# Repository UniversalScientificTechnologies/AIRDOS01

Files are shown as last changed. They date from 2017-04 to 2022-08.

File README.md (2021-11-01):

# Airborne dosimeter device - AIRDOS

Cosmic radiation dosimeter unit. It is intended for airborne measurement of cosmic radiation and dosimetry in mixed ionization fields on board of aircraft. 

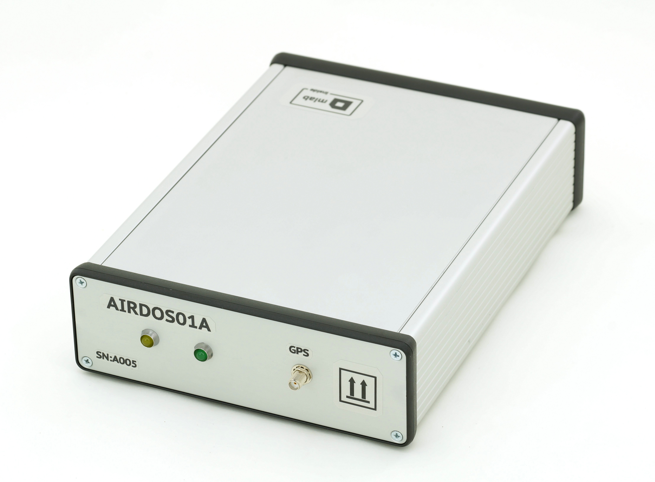
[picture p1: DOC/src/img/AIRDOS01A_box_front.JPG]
AIRDOS01A Front panel with indicating LEDs and GPS antenna connector AIRDOS Front panel


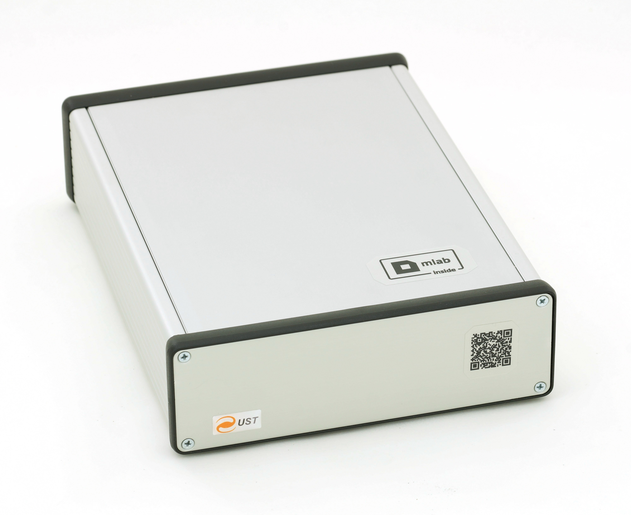
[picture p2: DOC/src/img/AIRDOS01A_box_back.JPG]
AIRDOS01A back panel AIRDOS back panel


Technical parameters are following: 

* Silicon PIN diode detector with 60mm³ detection volume
* Measurement endurance 32 days
* Number of erengy channels    252
* Energy measurement resolution    <30 keV/channel
* GPS logging interval    5 minutes
* Time to GPS fix	26 s
* Airborne GPS parameters (Navigation altitude verified up to 36km amsl)
* Integration time    8 s
* Weight 1.225 kg (Without batteries and GPS antenna)

Device block diagram
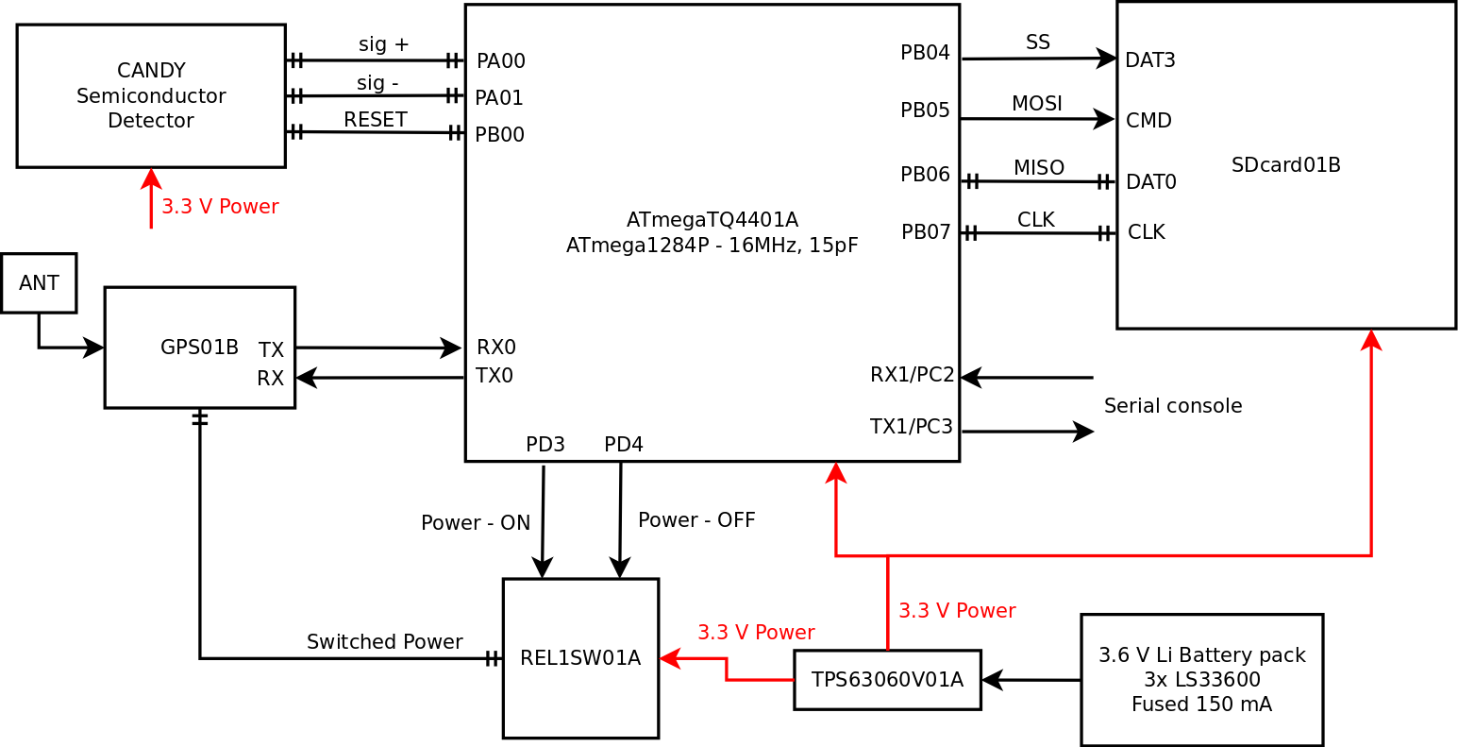
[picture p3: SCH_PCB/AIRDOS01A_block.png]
AIRDOS01A back panel


CANDY detector schematics
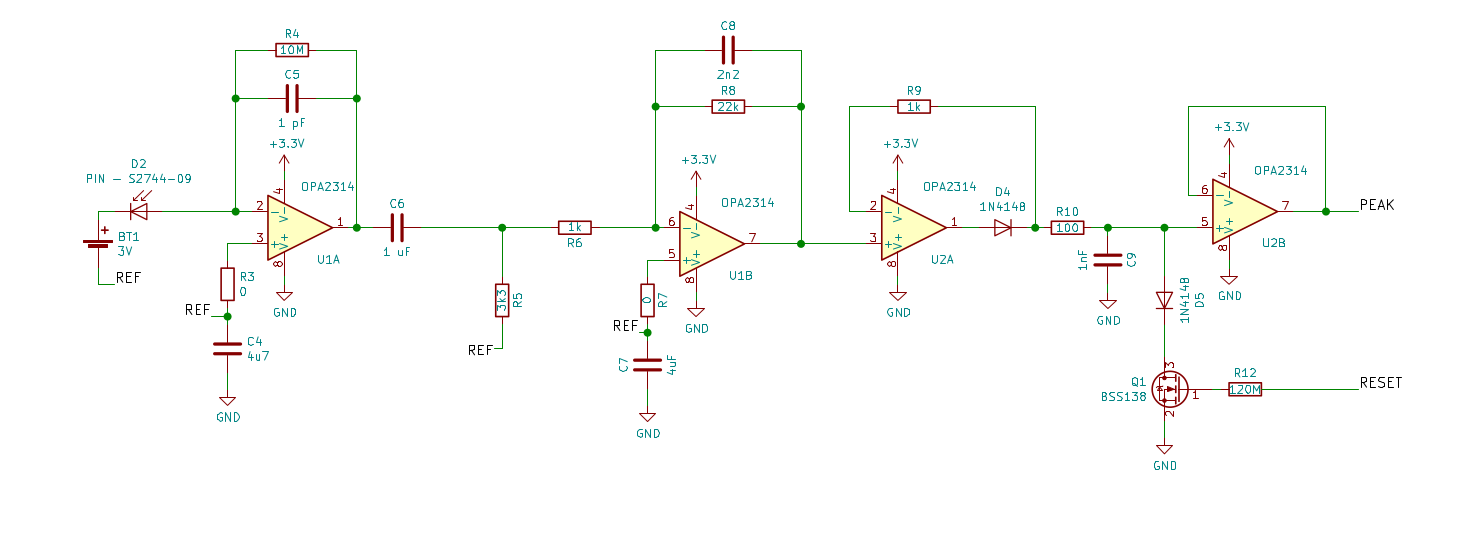
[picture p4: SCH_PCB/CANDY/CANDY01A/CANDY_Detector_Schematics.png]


The device is replaced with updated version [AIRDOS02](https://github.com/UniversalScientificTechnologies/AIRDOS02).

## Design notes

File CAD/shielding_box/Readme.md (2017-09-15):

# Manufacturing process

The models could be printed from PLA plastic. The used color filling probably affects intsrument sensitivity. Use of natural PLA material is recommended. 

  * Parts must be coated by copper conductive layer
  * Printed parts need cleanup after printing. Cleanup is mandatory operation before coating.

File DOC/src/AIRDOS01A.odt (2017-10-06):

AIRDOS01E

Seznam materiálu:

GPS01B

-JUMP -EXT

-USB-OFF

-ACTIVE

REL1SW01A

-JUMP -VCC-1

-1-2

-VCC-10

TPS63060V01A

-JUMP -EN-VIN

-MODE

-3,3V

ATMEGATQ4401A

-krystal 16MHz

SDcard01B

-bez LED

M3x14 8ks – na OZDUAL03B -dotahují se pak všechny matky, nesmí se nic klepat

Přední panel boxu:

Pořadí prvků na panelu z leva do prava: LED ŽLUTÁ, LED ZELENÁ, SMA

LED ZELENÁ – 5mm, odpor na anodu 1kΩ, vodiče 10 cm

LED ZELENÁ/A – GPS01B/TIMEPULSE – zelená

LED ZELENÁ/K – GPS01B/GND – modrá

LED ŽLUTÁ – 5mm, odpor na anodu 1kΩ, vodiče 13 cm

LED ŽLUTÁ/A – ATMEGATQ4401A/VCC – žlutá

LED ŽLUTÁ/K – ATMEGATQ4401A/PC7 – modrá

OZDUAL03B č.1

-JUMP -GNDA-GND

Baterka 3V

-přidělané káblíky 4,5 cm, žlutá +, modrá -. Konektroy na hřebínek na konci.

Baterkové pouzdro na 3 baterie

-kabel s pojistkou + 5 cm kabelu – červená

-20cm - modrá

OZDUAL03B č.2

-JUMP - GNDA-GND

- 5 – 4

- OUTA – INA-

Detektor

ATMEGATQ4401A – OZDUAL03B č.1

PA1 – INB+ - bílá 15 cm

ATMEGATQ4401A – OZDUAL03B č.2

PB0 – 1 - fialová 15 cm

GND – GNDA - modrá 15 cm

VCC – VIN+ - červená 15cm

PA0 – OUTB – žlutá 15cm

Baterie 3V – OZDUAL03B č.1

- - INA+ - žlutá

+ - VREF – modrá

OZDUAL03B č.2 – OZDUAL03B č.1

POWER – POWER – vodič modrý a červený 10 cm

VREFA – OUTB – žlutá 10 cm

OZDUAL03B č.2

VREFB – 2 – šedá 10 cm

INB+ - OUTA – žlutá 10 cm

OZDUAL03B č.1

VREFA – 2 – 4 – INB+ - fialová 10 cm

VREFB – OUTA – žlutá 10 cm

ATMEGATQ4401A

AREF – PA1 – bílá 10 cm

PC2 – VCC – oranžová 10 cm

10K (proti přívodu z GPS) – PD0 – oranžová 10 cm

ATMEGATQ4401A – Sdcard01B

PB7 – J4 – fialová 15 cm

PB6 – J5 – bílá 15 cm

PB5 – J3 – oranžová 15 cm

PB4 – J8 – šedá 15 cm

POWER – POWER 3,3V – modrá/červená 20 cm

ATMEGATQ4401A – TPS63060V01A

POWER – POWER OUT – červená/modrá 10 cm

RELL1SW01A – ATMEGATQ4401A

IN2 – PD3 – bílá 10 cm

IN1 – PD4 – šedá 10 cm

RELL1SW01A

5 – OUT1 – zelená 10 cm

6 – OUT2 – fialová 10 cm

RELL1SW01A – TPS63060V01A

POWER – POWER IN – červená/modrá 10 cm

RELL1SW01A – GPS01B

POWER (-) – POWER – modrá 10 cm

3 – POWER – červená 10 cm

GPS01B – ATMEGATQ4401A

TXD – 10k – oranžová 10 cm

RXD – PD1 – žlutá 10 cm

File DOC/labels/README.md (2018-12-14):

### Samolepky na přístroj AIRDOS

Samolepky jsou vytištěné na laminovaných páskách  TZE-111, TZE-121 a TZE-151. 

Po vytištení je potřeba samolepkám diagonálně zastřihnout rohy, aby bylo snížena možnost jejich odloupnutí.  Na přístroj se samolepky lepí podle následujících obrázků.

**Povrch přístroje je potřeba před lepením odmastit gázovým čvercem namočeným v alkoholu!**

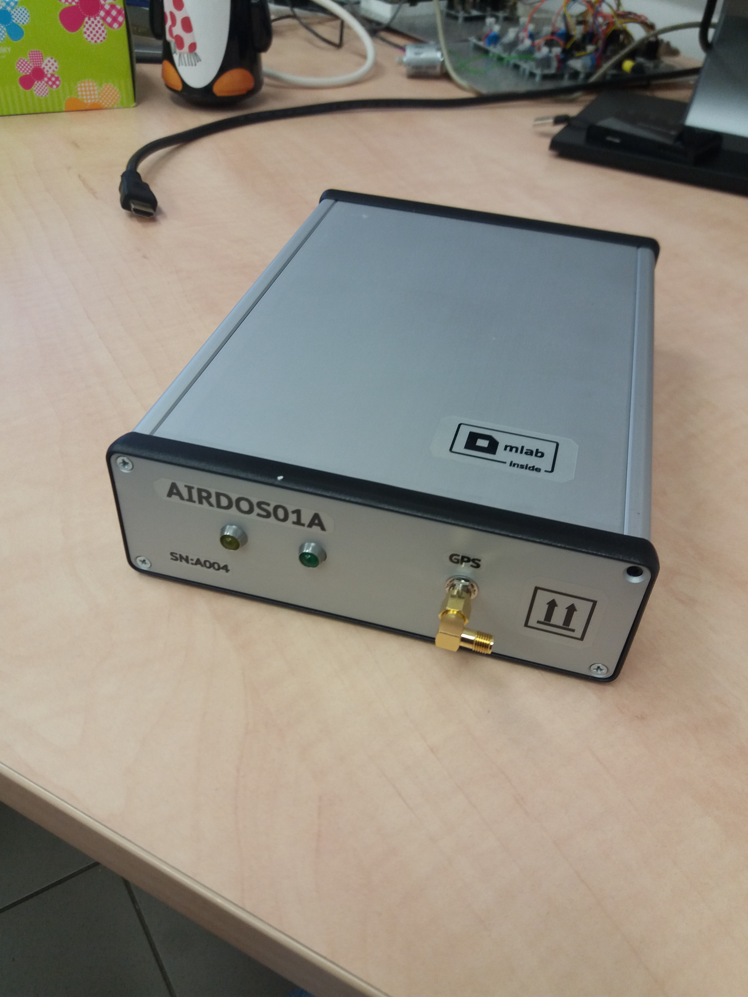
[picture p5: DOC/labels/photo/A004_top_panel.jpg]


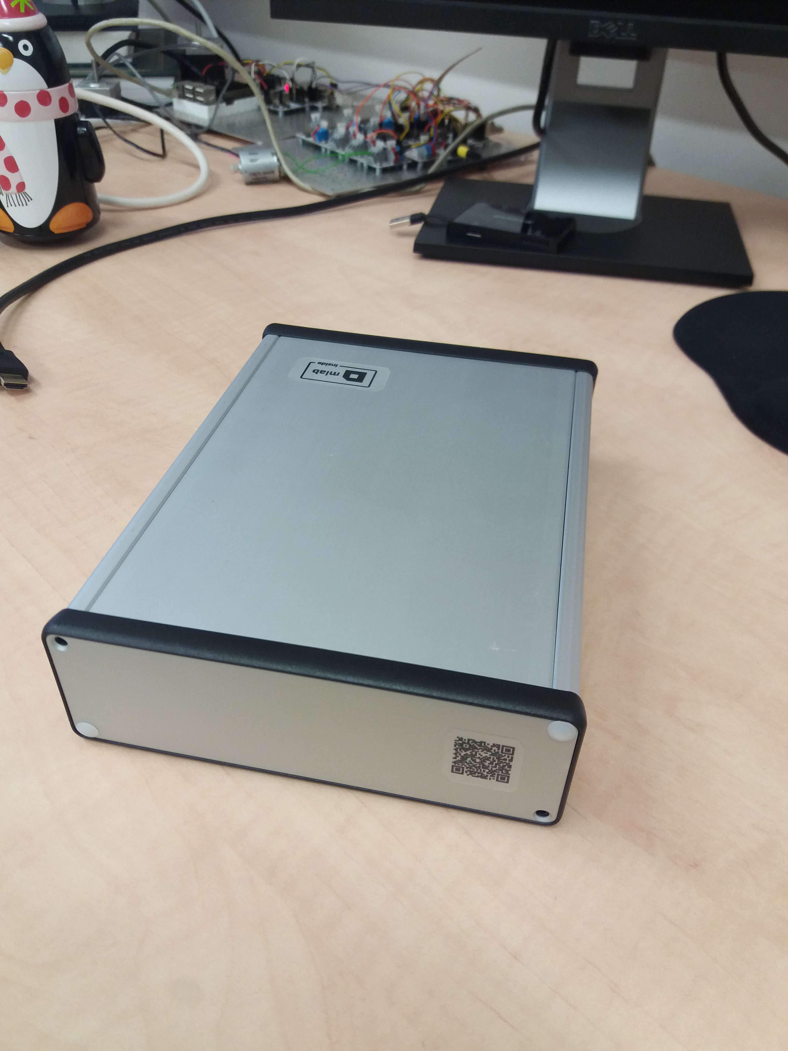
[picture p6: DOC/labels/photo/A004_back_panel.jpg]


Kromě těchto vnitřních samolepek existují ještě vnitřní samolepky se seriovými čísly, které jsou nalepeny na vnitřní stranu vyjmutelných plechových dílů. 

### Generování QRkódů

QR kód se generuje spuštěním příkazu

    ./generate_QR.sh

Ještě před tím je ale potřeba ve skriptu nastavit obsah, který má QRkód obsahovat. 

Tím vznikne soubor AIRDOS01-QRcode.svg, který obsahuje aktualizovaný QRkód. 
Tento soubor je prolinkován se souborem QRcode_24x24.svg ve kterém by se měl automaticky aktualizovat při otevření souboru. 

Soubor QRcode_24x24.pdf je nutné ručně exportovat.

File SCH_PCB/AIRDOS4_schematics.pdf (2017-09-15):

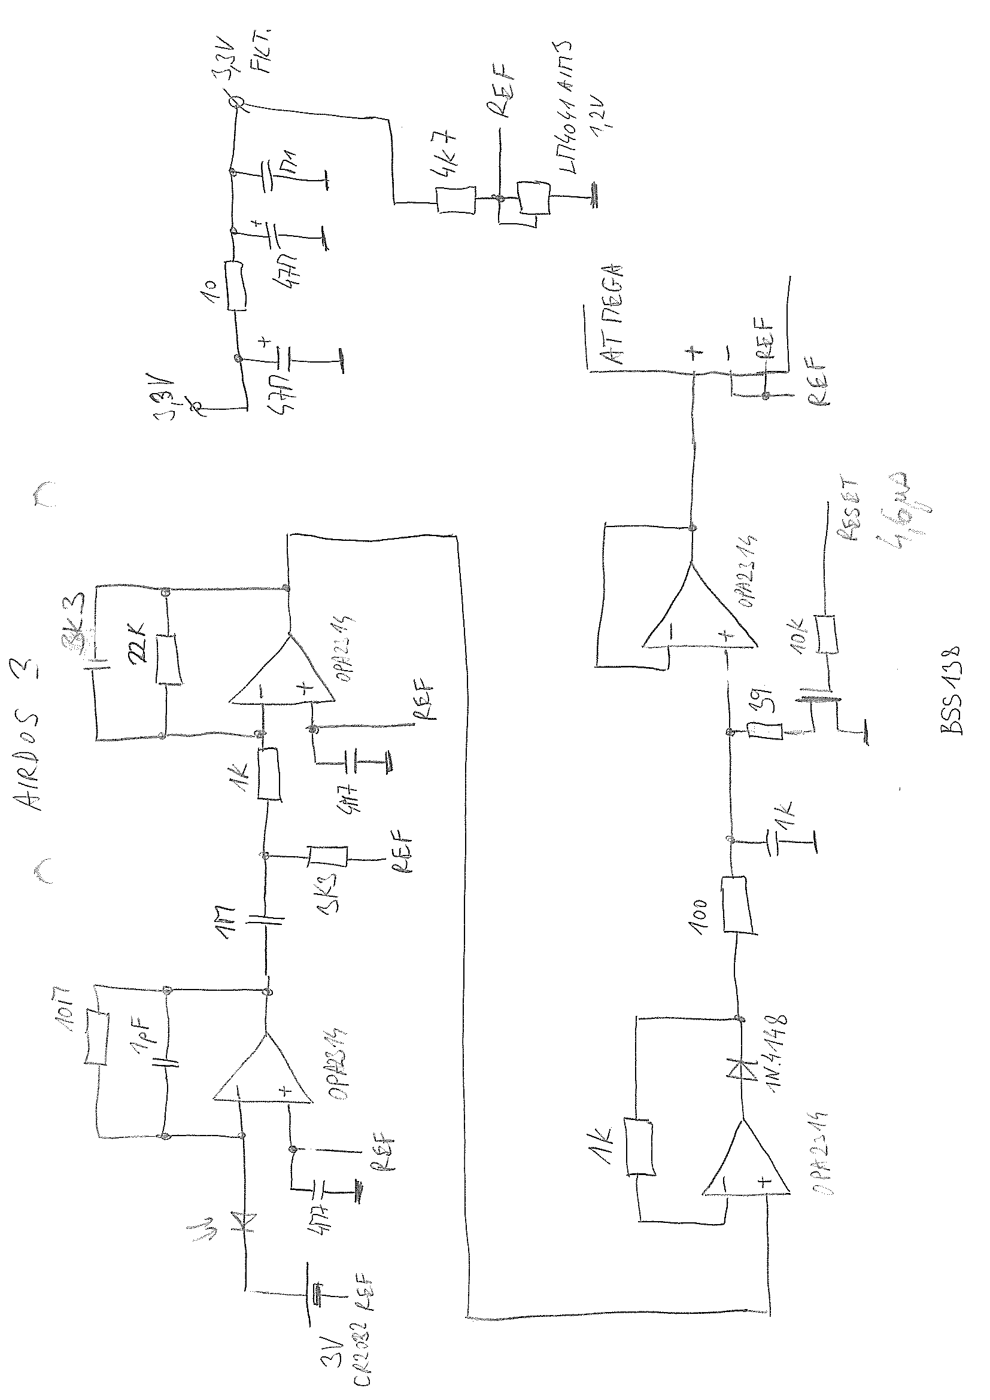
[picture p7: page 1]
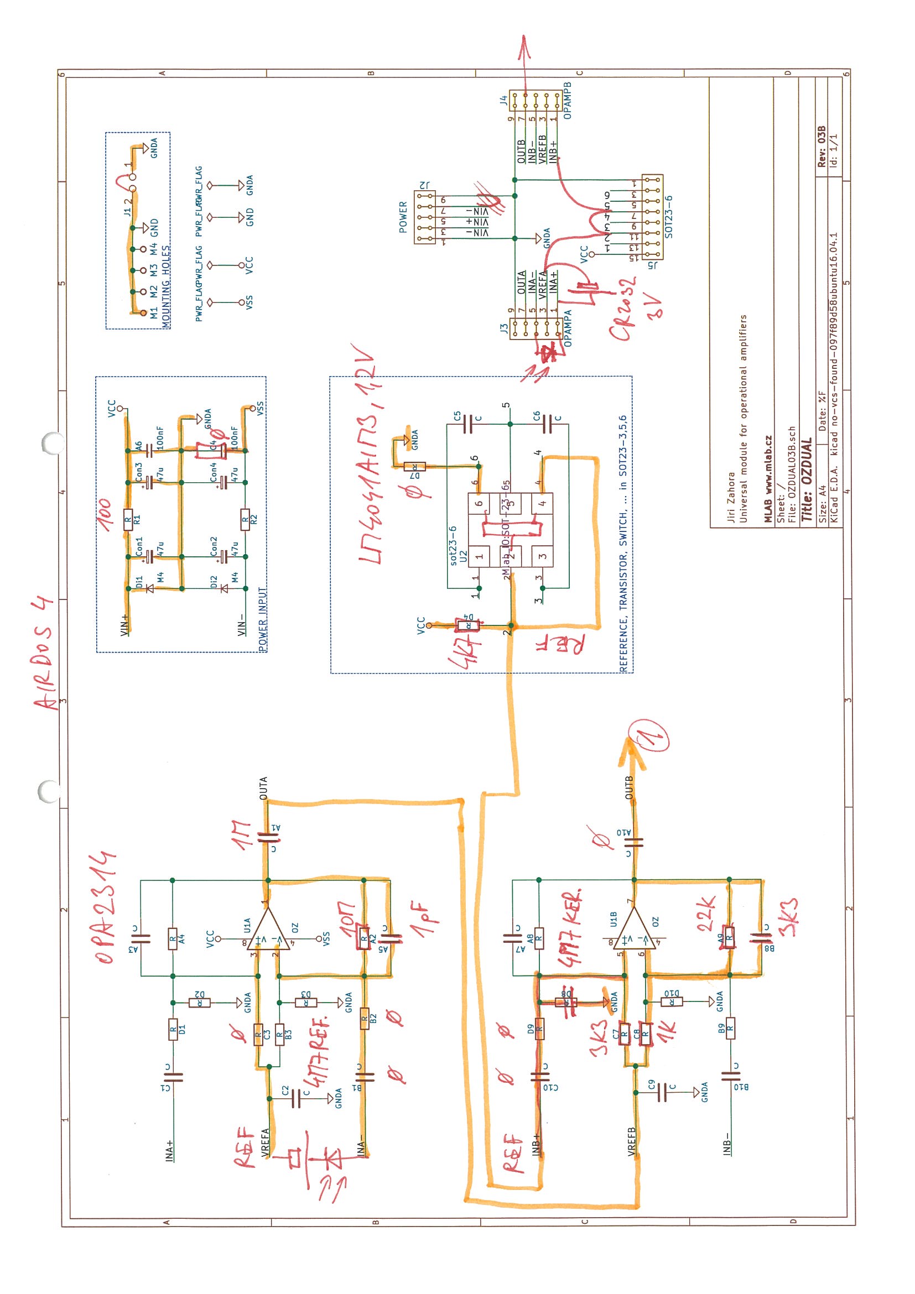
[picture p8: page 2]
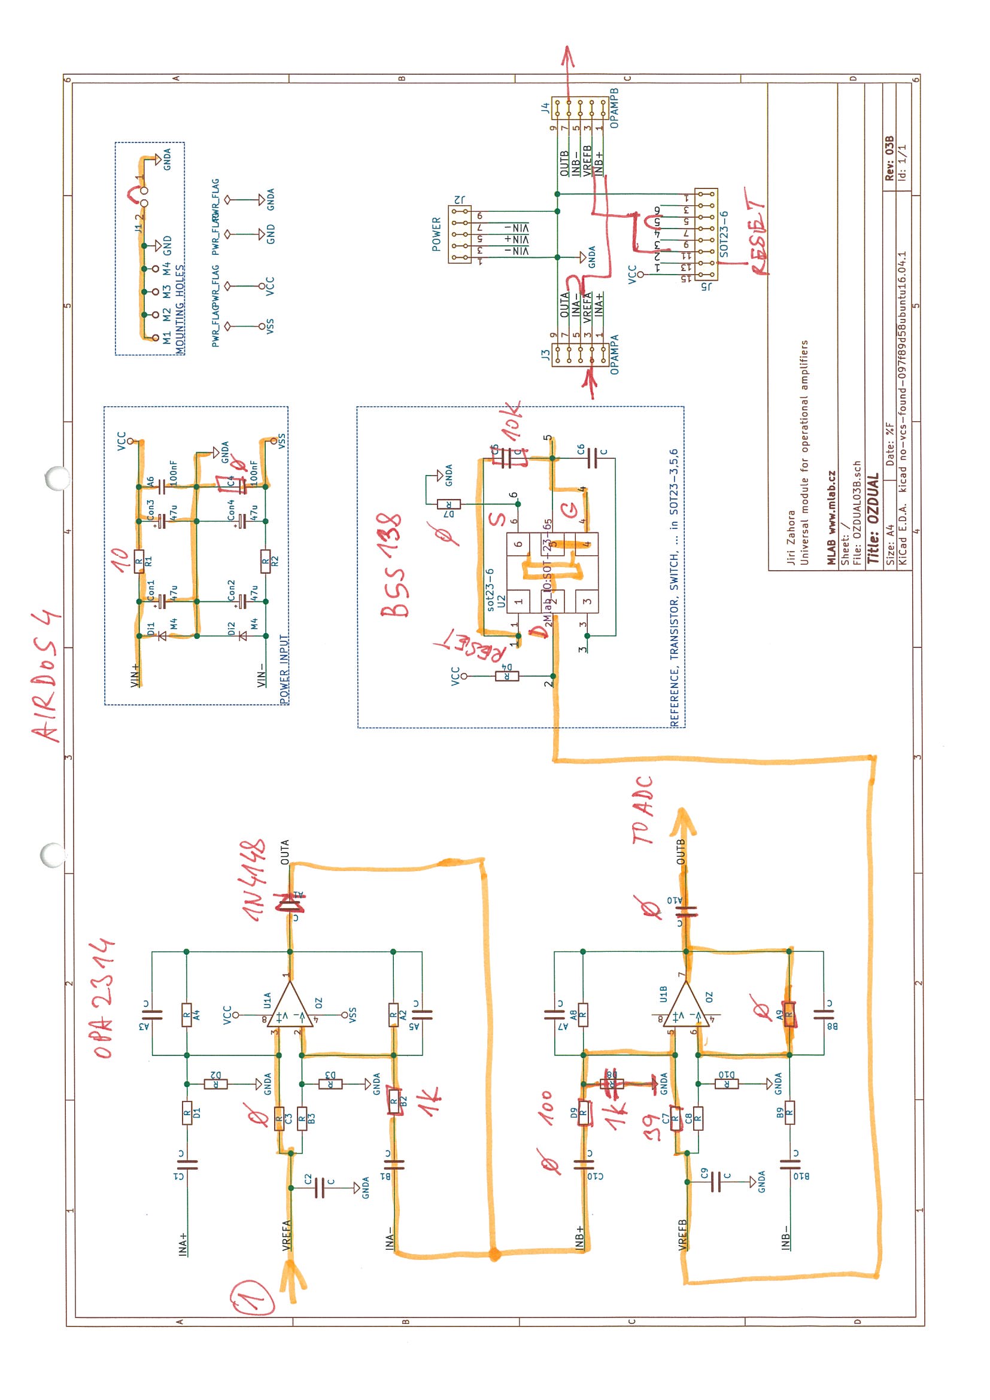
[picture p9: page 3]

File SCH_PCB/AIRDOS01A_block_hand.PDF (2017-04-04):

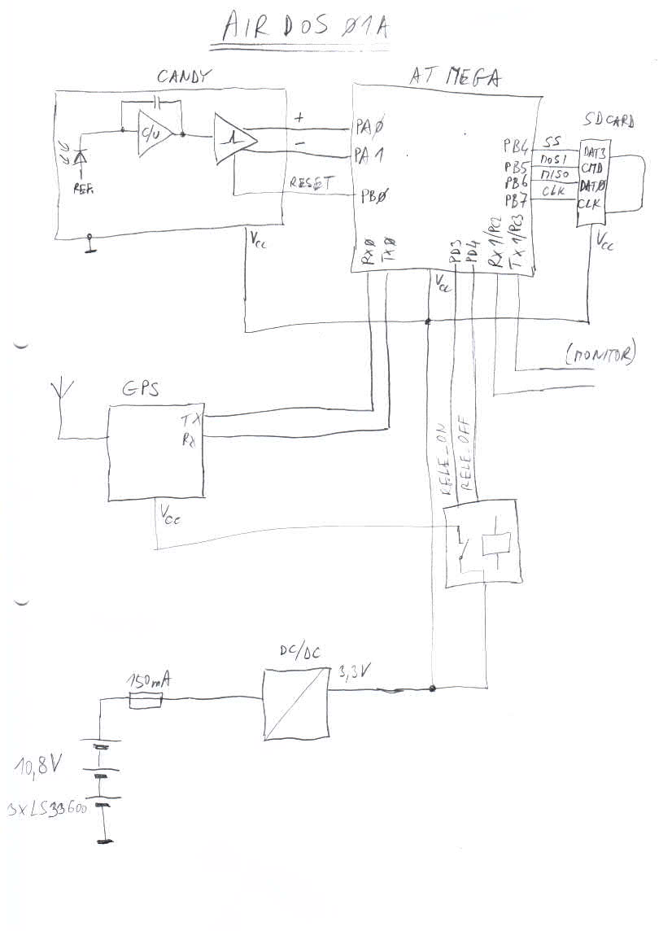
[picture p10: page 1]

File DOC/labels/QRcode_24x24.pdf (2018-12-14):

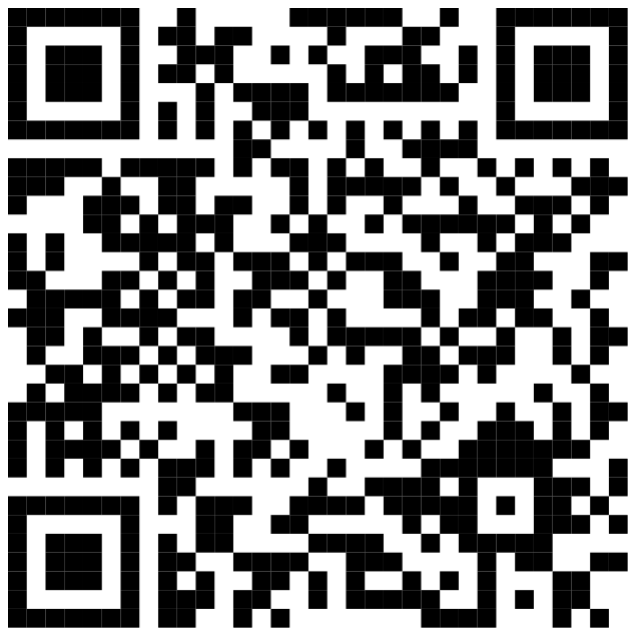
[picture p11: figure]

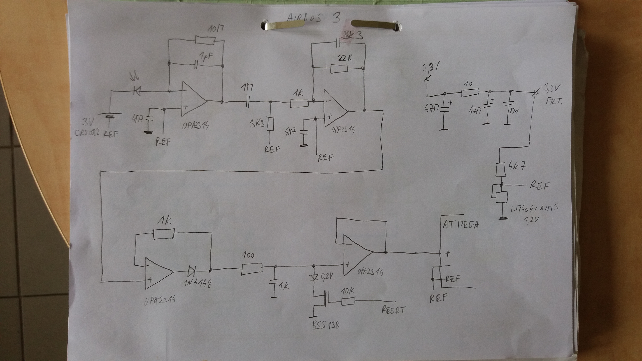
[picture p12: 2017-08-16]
SCH_PCB/AIRDOS3_Schematics.jpg

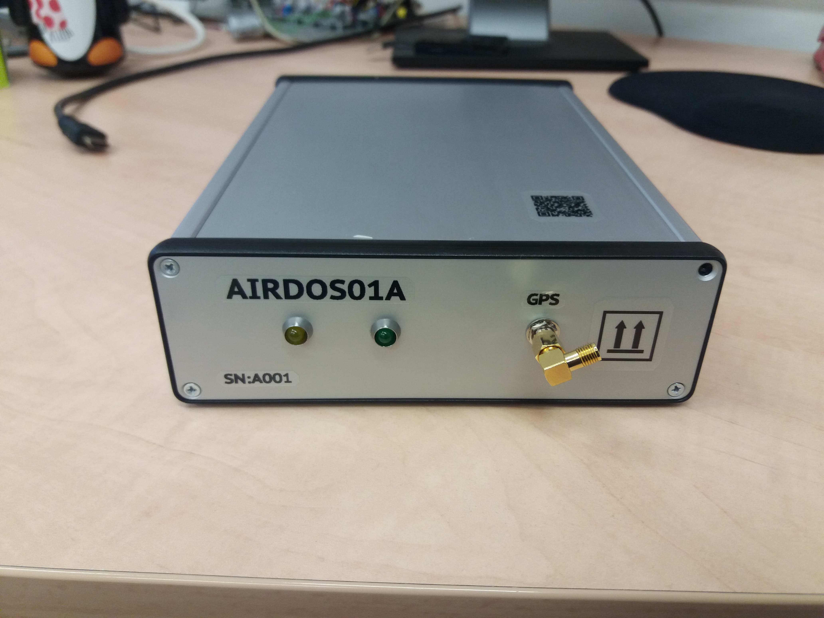
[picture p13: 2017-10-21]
DOC/labels/photo/A001_front_panel.jpg

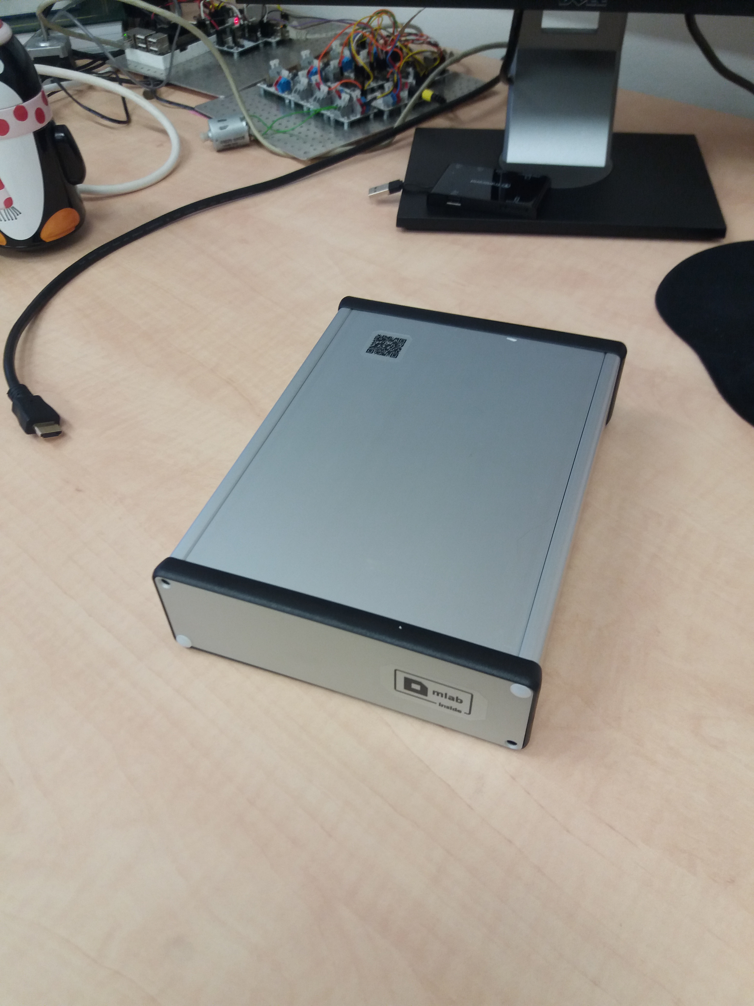
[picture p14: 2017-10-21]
DOC/labels/photo/A001_back_panel.jpg

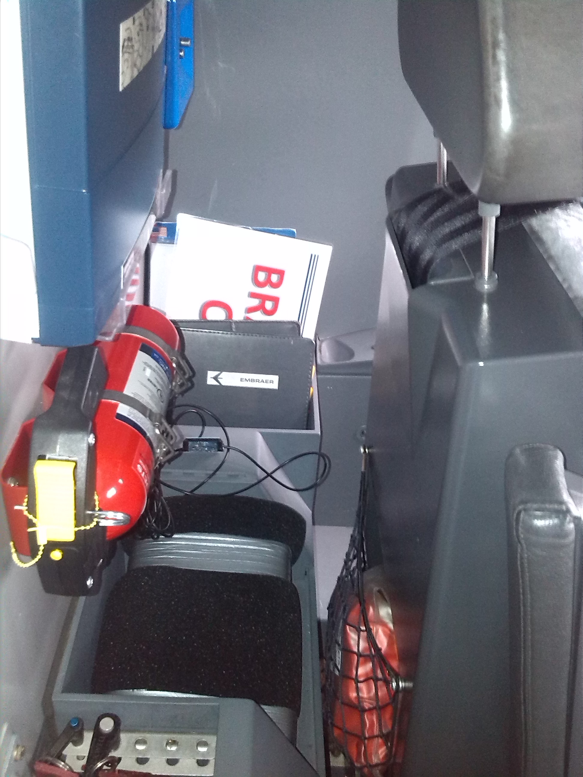
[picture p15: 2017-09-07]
DOC/src/img/AIRDOS01A_in_use.jpg

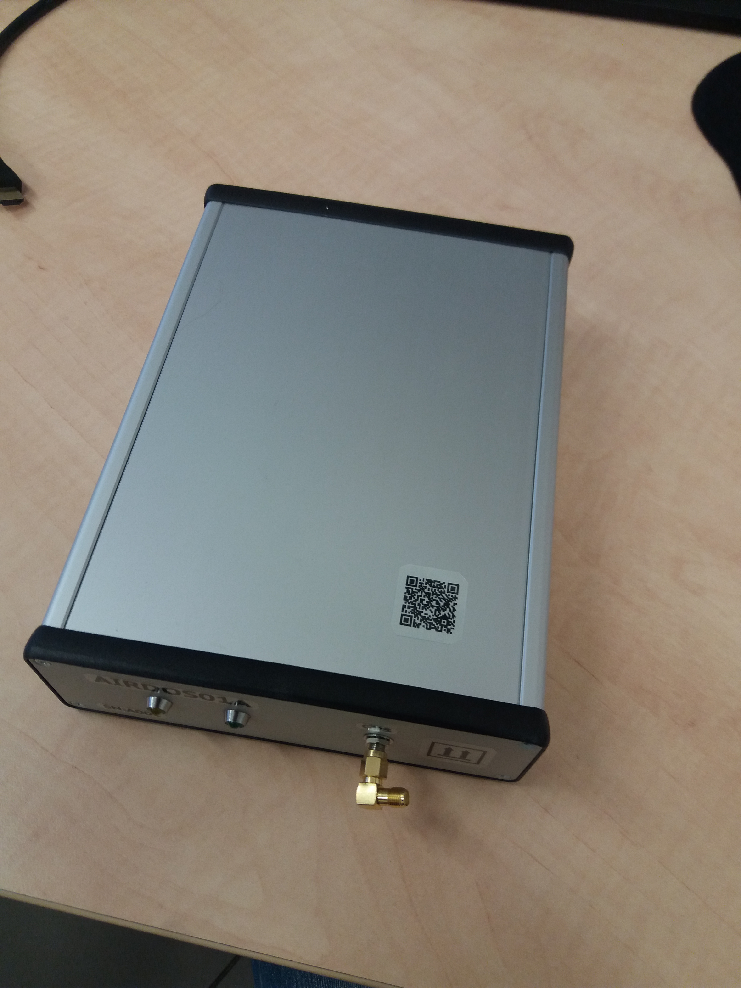
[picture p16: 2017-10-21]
DOC/labels/photo/A001_top_cover.jpg

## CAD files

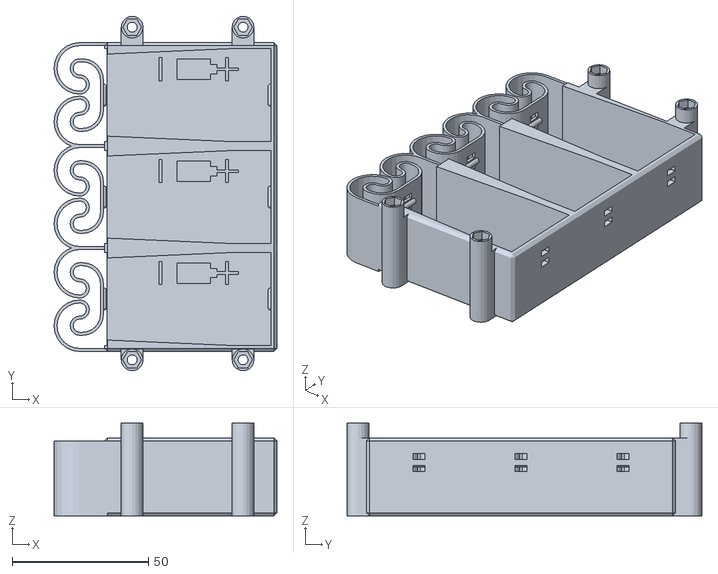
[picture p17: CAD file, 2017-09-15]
CAD/Battery_holder/AMF/P_AIRDOS_batter_body.stl
81.7 x 129.9 x 34.0

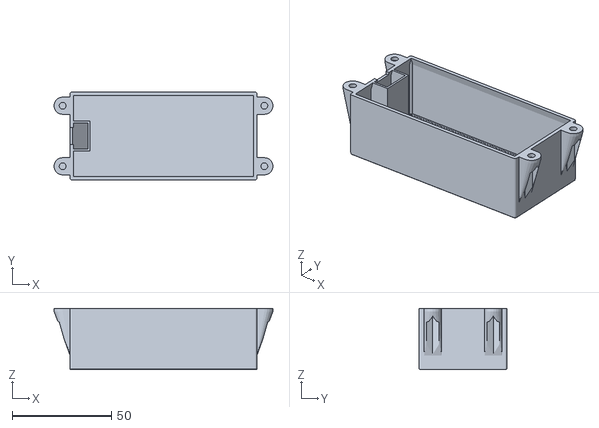
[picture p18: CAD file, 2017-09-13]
CAD/shielding_box/Box.stl
110.3 x 44.2 x 30.9

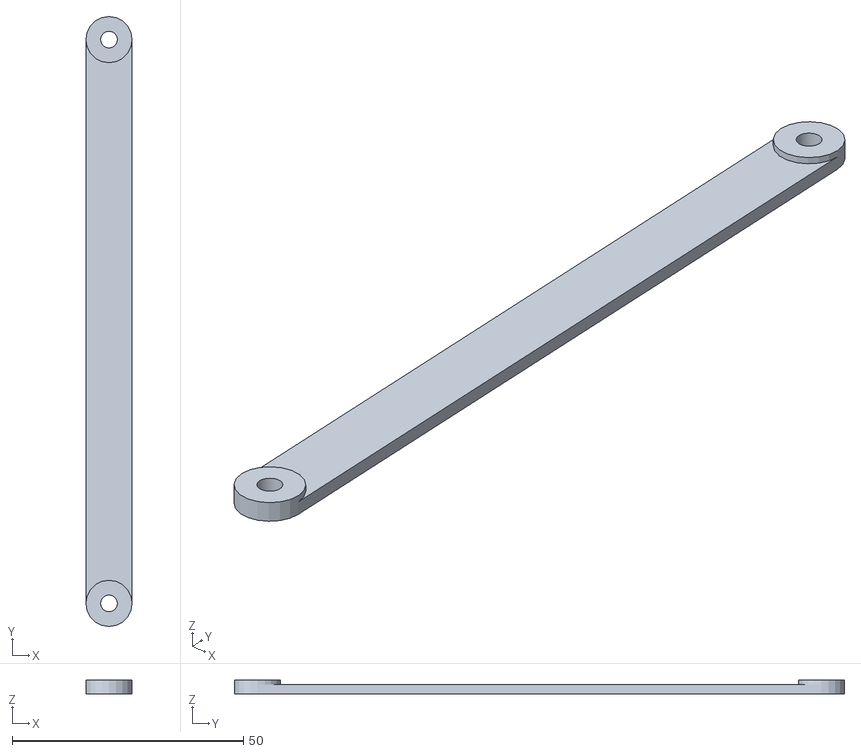
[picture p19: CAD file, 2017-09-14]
CAD/Battery_holder/AMF/P_AIRDOS_batter_belt.stl
10.0 x 131.9 x 3.00

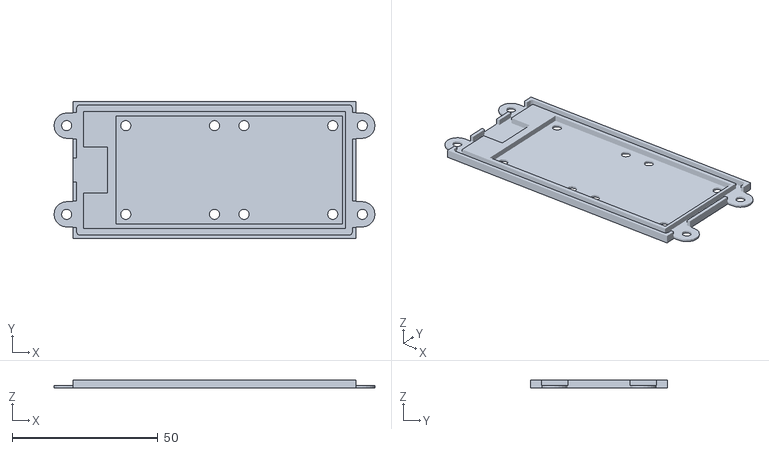
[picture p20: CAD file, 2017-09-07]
CAD/shielding_box/BoxBase.stl
110.3 x 47.2 x 2.80

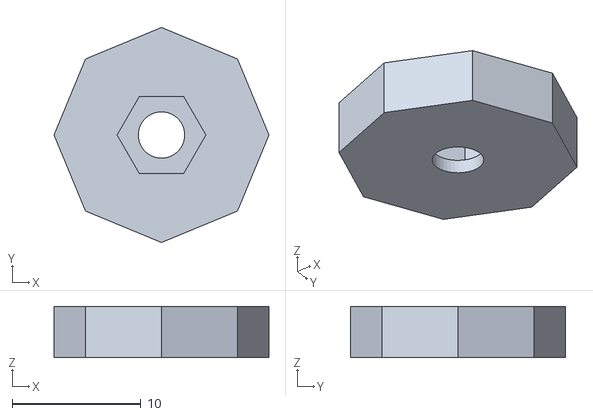
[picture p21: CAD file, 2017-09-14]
CAD/Battery_holder/AMF/P_AIRDOS_batter_nut.stl
16.7 x 16.7 x 4.00

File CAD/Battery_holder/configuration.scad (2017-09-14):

//Parametry sroubu
prumer_sroubu=3.4;
prumer_hlavy_sroubu=6;
vyska_hlavy_sroubu=4;
vyska_matky=3;
sirka_matky=6.7;

baterka_prumer=33;
baterka_delka=60;


vyska_sloupku=baterka_prumer+1;
sila_materialu=1.3;

pocet_poli_mezi_srouby=12;

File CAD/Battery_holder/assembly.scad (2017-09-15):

use <src/flexbatter.scad>
use <src/AIRDOS_batter.scad>

include <configuration.scad>


AIRDOS_prezentace();

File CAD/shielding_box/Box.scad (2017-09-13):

h = 30;      // Výška horní části
s = 4;      // Výška spodní části
a = 4;       // Šířka krabičky (počet obsazených dírek)
b = 9;      // Délka krabičky (počet obsazených dírek)
d = 1.8;     // Průměr trnů a šířka hlavních příček (>1)
c = 0.8;   // Tloušťka stěn

drat = 1.5;  // Průměr/výška otvoru na dráty

okraj = 2;  // šířka horního okraje

clear = 0.4;      // K otvoru na matičku
nut_size = 6.6;     // K otvoru na matičku

MLAB_grid = 10.16;
pedestal_height = 2; 

ot = 6*MLAB_grid/11;         //Vzdálenost okraje od děr v plošňáku pro stranu s tunelem
o = MLAB_grid/2+d/2;   //Vzdálenost zbylých okrajů od děr v plošňáku



$fn=20;

roh =0.5; // Zaoblení hran

// Kvádr a válec se zaoblenými hranami
module roundcube(size,center=true,corner) {
  minkowski() {
    cube(size,center);
    sphere(corner);
  }
}

module roundcylinder(size, r, center=true, corner) {
  minkowski() {
    cylinder(size, r, r, center);
    sphere(corner);
  }
}







module konstrukce1()
{
  difference() {
  union() {
      // Hlavní příčky
     translate([0,(MLAB_grid*(a-1))/2+o,0]) 
      roundcube([d-2*roh, MLAB_grid*(a-1)+2*o, d-2*roh],center = true, corner= roh);
     
     translate([(MLAB_grid*(b-1))/2+ot,0,0])       
      roundcube([MLAB_grid*(b-1)+2*ot, d-2*roh, d-2*roh],corner= roh); 
      
     translate([0, 0, h/2])
      cylinder(h, d/2, d/2, center = true);
      
 /*     //Vedlejší příčky - ve směru x
      for(i = [1:a]) {
     translate([(MLAB_grid*(b-1))/2+ot ,o + MLAB_grid*(i-1),-d/4+roh/2])
      roundcube([MLAB_grid*(b-1)+2*ot,d-2*roh,(d-2*roh)/2],corner = roh);
      }
      //Vedlejší příčky - ve směru y
      for(i = [1:b]) {
     translate([ot + MLAB_grid*(i-1), (MLAB_grid*(a-1))/2+o, -d/4+roh/2])
      roundcube([d-2*roh, MLAB_grid*(a-1)+2*o, (d-2*roh)/2],corner=roh);
      }
      //Vedlejší příčky - ve směru z
      for(i = [1:a]) {
     translate([0, o + MLAB_grid*(i - 1), h/2])
      difference() {
          cylinder(h, d/2, d/2, center = true);
          translate([d/2,0,h/2])
          cube([d,d,h/2+5], center = true);
      }
      }
      for(i = [1:b]) {
     translate([ot+MLAB_grid*(i-1), 0, h/2])
      cylinder(h, d/2, d/2, center = true);
      }
      
  */    
 // ZAOBLENI ROHU    
  hull() {
difference() {
            union() {
    translate([0,(MLAB_grid*(a+1))/2,0]) 
      roundcube([d-2*roh,MLAB_grid*(a+1),d-2*roh],center = true, corner= roh);
     
     translate([(MLAB_grid*(b+1))/2,0,0])       
      roundcube([MLAB_grid*(b+1),d-2*roh,d-2*roh],corner= roh); 
      
     translate([0, 0, h/2-d/2+2*roh])
      roundcylinder(h, (d/2-roh), corner = roh);
            }
      translate([0,(MLAB_grid*(a+1))/2 + d,0]) 
        cube([20*d,MLAB_grid*(a+1)+d,20*d], center = true);
     
      translate([(MLAB_grid*(b+1))/2 + d,0,0]) 
        cube([MLAB_grid*(b+1)+d,20*d,20*d], center = true);
            
      translate([0, 0, -d/2 + d])
        cylinder(h + d, 20*d);
        }
    }
   

 //Pacička

translate([ot-MLAB_grid, o,h-1.5]) {
    difference() {  
        hull() {
        translate([0,-3/7*MLAB_grid,0])
            cube([MLAB_grid-ot-0.2,2*3/7*MLAB_grid,1.5]);
            cylinder(1.5, 3/7*MLAB_grid, 3/7*MLAB_grid);
        translate([MLAB_grid-ot-c, -3/7*MLAB_grid, -3*h/4])
            cube([c-0.2, 2*3/7*MLAB_grid, 1.5]);
        }
    translate([0,0,1.5/2+0.4])   
    cylinder(3, 3.5/2, 3.5/2, center = true);
    translate([0,0,-h/2])
    rotate(0)
    cylinder (h-1.5, r= (nut_size+clear)/2, center = true, $fn=6);
    } 
}

  
}

/* // Oříznutí sloupků
translate([0,0, h - 10]) 
        cube([MLAB_grid*(b)+o,MLAB_grid*(a)+o,20*d]); */
    
/* //Pacička

translate([o-MLAB_grid, o,h -d/2]) {
    difference() {  
        union() {
    translate([0,-3.5,0])
    cube([MLAB_grid-o,2*3.5,d/2]);
    cylinder(d/2, 1/3*MLAB_grid, 1/3*MLAB_grid);
        }
        
    cylinder(h, 3.5/2, 3.5/2, center = true);
    } 
}
 
// Horní příčka k pacičce
translate([-d/2, 0, h - d/2])
    cube([d/2,MLAB_grid*(a-1)+2*o,d/2]);

*/

}







}
konstrukce1();

  



//Zrcadlení

translate([MLAB_grid*(b-1)+2*ot,0,0]) 
mirror(1,0,1) konstrukce1();
translate([0,MLAB_grid*(a-1)+2*o,0])
mirror([0,1,0]) konstrukce1();
translate([MLAB_grid*(b-1)+2*ot,0,0]) 
mirror(1,0,1)
translate([0,MLAB_grid*(a-1)+2*o,0])
mirror([0,1,0]) konstrukce1();



// Obal klece
    difference() {
        union() {
translate([-d/2,0,0]) 
cube([c, MLAB_grid*(a-1)+2*o, h]);

translate([0,-d/2,0]) 
cube([(MLAB_grid*(b-1))+2*ot, c, h]);

translate([0,0,-d/2]) 
cube([(MLAB_grid*(b-1))+2*ot, (MLAB_grid*(a-1))+2*o, c]);
            
translate([(MLAB_grid*(b-1))+2*ot+d/2-c,0,0]) 
cube([c, MLAB_grid*(a-1)+2*o, h]);

translate([0,(MLAB_grid*(a-1))+2*o+d/2-c,0]) 
cube([(MLAB_grid*(b-1))+2*ot, c, h]);
            
// Horní příčky
translate([okraj/2-d/2, (MLAB_grid*(a-1)+2*o)/2, h-1.5*okraj])
   difference() {
    cube([okraj,MLAB_grid*(a-1)+2*o,3*okraj], center = true);  
    translate([okraj/2,0,0])
    rotate([0,15,0])
    cube([okraj,MLAB_grid*(a-1)+2*o,10*okraj], center = true);   
   } 
        
translate([(MLAB_grid*(b-1))+2*ot-okraj/2+d/2, (MLAB_grid*(a-1)+2*o)/2, h - 1.5*okraj])
    difference() {
    cube([okraj,MLAB_grid*(a-1)+2*o, 3*okraj], center = true);
    translate([-okraj/2,0,0])    
    rotate([0,-15,0])
    cube([okraj,MLAB_grid*(a-1)+2*o,10*okraj], center = true);   
   } 
        
translate([(MLAB_grid*(b-1)+2*ot)/2, okraj/2-d/2, h - 1.5*okraj])
    difference() { 
   cube([MLAB_grid*(b-1)+2*ot, okraj, 3*okraj], center = true);
  
   translate([0,okraj/2,0])
    rotate([-15, 0, 0])
   cube([MLAB_grid*(b-1)+2*ot, okraj, 10*okraj], center = true);
   }
       
 translate([(MLAB_grid*(b-1)+2*ot)/2, (MLAB_grid*(a-1))+2*o-okraj/2+d/2, h - 1.5*okraj])
    difference() { 
   cube([MLAB_grid*(b-1)+2*ot, okraj, 3*okraj], center = true);
   translate([0,-okraj/2,0])
    rotate([15, 0, 0])
   cube([MLAB_grid*(b-1)+2*ot, okraj, 10*okraj], center = true);
   }
 
 
 // Tunel
   translate([MLAB_grid/2-d/2, (MLAB_grid*(a-1)+2*o)/2, h/2-d/4])
    difference() { 
   cube([MLAB_grid,1.5*MLAB_grid,h+d/2], center = true);
   translate([0,0,0]) {
        
   cube([MLAB_grid-2,1.5*MLAB_grid-2,h+2], center = true); }
   translate([-MLAB_grid/2+d/2-1,0,-h/2+d/4-1]) {
   cube([d+1, 2*MLAB_grid, d+1], center = true); }
   translate([4,0,(-h+8)/2])
   cube([10,MLAB_grid,13], center = true);    
/* intersection(){
       translate([0,0,-h/2+9])
       rotate([225+20,0,0]) 
        cube([10,10,10]);
       translate([0,0,-h/2+9])
       rotate([225-20,0,0]) 
        cube([10,10,10]);} */
   }
   // Skluzavka v tunelu
   translate([0, (MLAB_grid*(a-1)+2*o)/2-0.75*MLAB_grid, 0])   
        difference() { 
   cube([MLAB_grid-2,1.5*MLAB_grid,(h+d/2)/3]);
   translate([0,0,(h+d/2)/3])
   rotate([0, 50, 0]) {
        
   cube([3*MLAB_grid-2,3*MLAB_grid,(h+d/2)]); }
   }
   
/*   
    translate([2.5*okraj-d/2, (MLAB_grid*(a-1)+2*o)/2, h-6*okraj-drat-1])
    difference() { 
   cube([5*okraj,MLAB_grid,12*okraj], center = true);
   translate([2.5*okraj,0,0])
    rotate([0, 20, 0])
   cube([5*okraj,MLAB_grid+1,15*okraj], center = true);
   }
   
  translate([2.5*okraj-d/2, (MLAB_grid*(a-1)+2*o)/2-MLAB_grid/2+d/4, h-(drat+1)/2])
   cube([5*okraj-1.9,d/2,drat+1], center = true);  
  
  translate([2.5*okraj-d/2, (MLAB_grid*(a-1)+2*o)/2+MLAB_grid/2-d/4, h-(drat+1)/2])
   cube([5*okraj-1.9,d/2,drat+1], center = true);
  
  translate([5*okraj-1.57-d/2, (MLAB_grid*(a-1)+2*o)/2, h-drat-1/2])
   cube([d/2,MLAB_grid,1], center = true);  */
    
        }    
        
//Otvor na dráty
        translate([-5, ((MLAB_grid*(a-1))+2*o)/2,h])
    cube([13,MLAB_grid-d,2*drat],center=true);      
     
/*  translate([2.5*okraj-d/2, (MLAB_grid*(a-1)+2*o)/2, h])
   cube([5*okraj-1.9,MLAB_grid,2], center = true);     */
           
        
/*    translate([-5, ((MLAB_grid*(a-1))+2*o)/2,h])
    rotate([0,90,0])
    cylinder(10, drat/2, drat/2, centre=true);
        
    translate([-5, ((MLAB_grid*(a-1))+2*o)/2+drat,h])
    rotate([0,90,0])
    cylinder(10, drat/2, drat/2, centre=true);
        
    translate([-5, ((MLAB_grid*(a-1))+2*o)/2-drat,h])
    rotate([0,90,0])
    cylinder(10, drat/2, drat/2, centre=true);
    
    translate([-5, ((MLAB_grid*(a-1))+2*o)/2-2*drat,h])
    rotate([0,90,0])
    cylinder(10, drat/2, drat/2, centre=true);
        
    translate([-5, ((MLAB_grid*(a-1))+2*o)/2+2*drat,h])
    rotate([0,90,0])
    cylinder(10, drat/2, drat/2, centre=true); */
    }
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

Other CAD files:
CAD/shielding_box/BoxBase.scad
CAD/Battery_holder/print_data/P_AIRDOS_batter_belt.scad
CAD/Battery_holder/print_data/P_AIRDOS_batter_body.scad
CAD/Battery_holder/print_data/P_AIRDOS_batter_nut.scad
CAD/Battery_holder/src/AIRDOS_batter.scad
CAD/Battery_holder/src/MLAB_logo.scad
CAD/Battery_holder/src/flexbatter.scad

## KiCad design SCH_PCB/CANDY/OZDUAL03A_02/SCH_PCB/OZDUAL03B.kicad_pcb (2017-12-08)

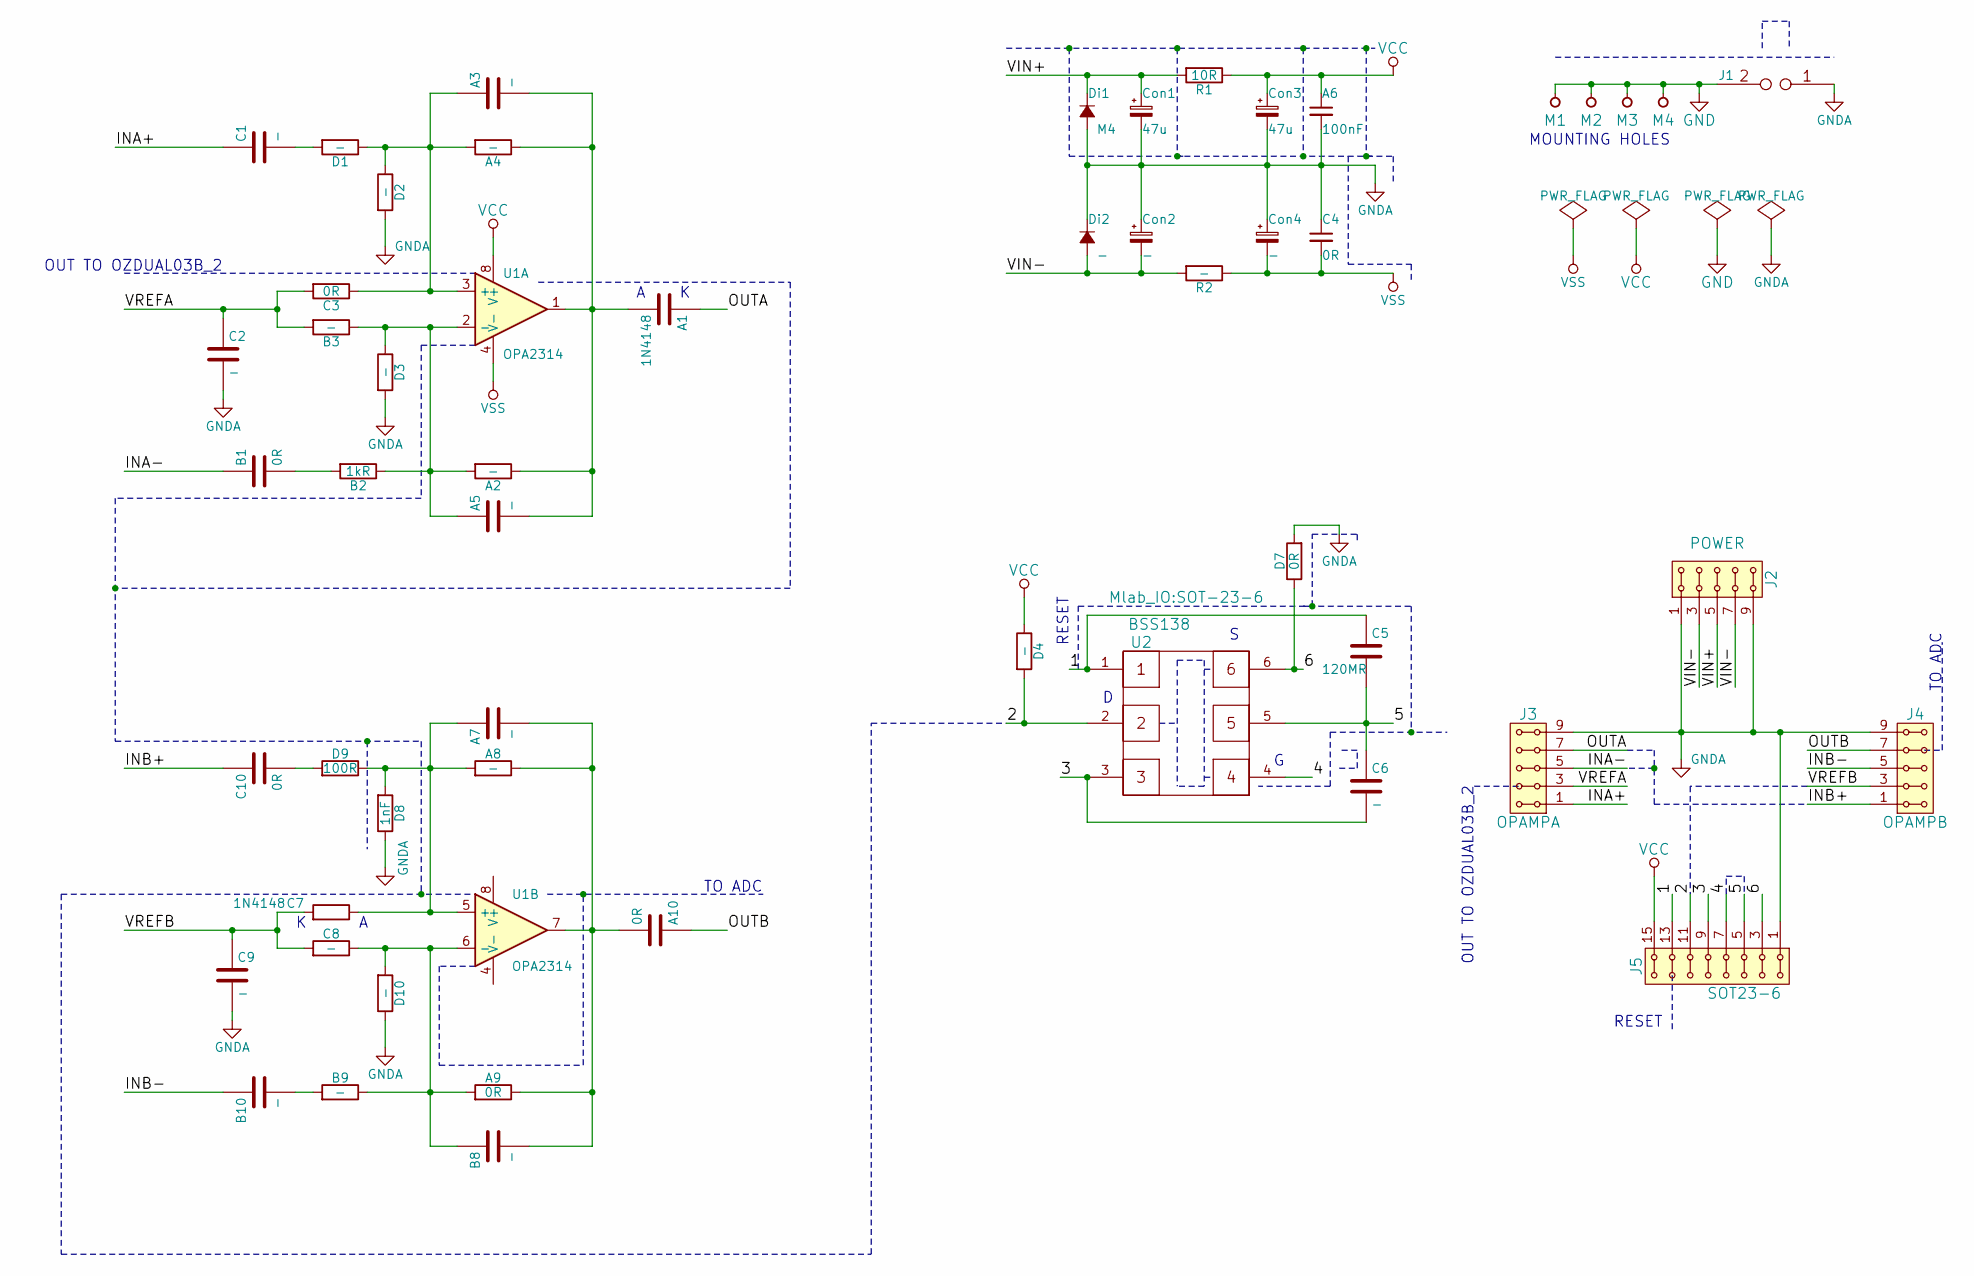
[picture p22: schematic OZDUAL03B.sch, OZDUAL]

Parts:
A1: 1N4148; SMD-0805-hand-soldering
A2, A3, A4, A5, A7, A8: -; SMD-0805-hand-soldering
A6: 100nF; SMD-0805-hand-soldering
A9, A10: 0R; SMD-0805-hand-soldering
B1: 0R; SMD-0805-hand-soldering
B2: 1kR; SMD-0805-hand-soldering
B3, B8, B9, B10: -; SMD-0805-hand-soldering
C1, C2, C6, C8, C9: -; SMD-0805-hand-soldering
C3, C4, C10: 0R; SMD-0805-hand-soldering
C5: 120MR; SMD-0805-hand-soldering
C7: 1N4148; SMD-0805-hand-soldering
Con1, Con3: 47u; TantalC_SizeC_Reflow
Con2, Con4: -; TantalC_SizeC_Reflow
D1, D2, D3, D4, D10: -; SMD-0805-hand-soldering
D7: 0R; SMD-0805-hand-soldering
D8: 1nF; SMD-0805-hand-soldering
D9: 100R; SMD-0805-hand-soldering
Di1: M4; Diode-SMA_Standard
Di2: -; Diode-SMA_Standard
J1: JUMP2_2x1; Straight_2x01
J2: POWER; Straight_2x05
J3: OPAMPA; Straight_2x05
J4: OPAMPB; Straight_2x05
J5: SOT23-6; Straight_2x08
M1, M2, M3, M4: HOLE; MountingHole_3mm
R1: 10R; SMD-0805-hand-soldering
R2: -; SMD-0805-hand-soldering
U1: OPA2314; SO-8
U2: BSS138; SOT-23-6

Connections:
/1: C5.1, J5.13, J5.14, U2.1
/2: D4.2, J5.11, J5.12, U2.2
/3: C6.2, J5.9, J5.10, U2.3
/4: J5.7, J5.8, U2.4
/5: C5.2, C6.1, J5.5, J5.6, U2.5
/6: D7.1, J5.3, J5.4, U2.6
/INA+: C1.1, J3.1, J3.2
/INA-: B1.1, J3.5, J3.6
/INB+: C10.1, J4.1, J4.2
/INB-: B10.1, J4.5, J4.6
/OUTA: A1.1, J3.7, J3.8
/OUTB: A10.1, J4.7, J4.8
/VIN+: Con1.1, Di1.1 (K), J2.5, J2.6, R1.2
/VIN-: Con2.2, Di2.2 (A), J2.3, J2.4, J2.7, J2.8, R2.2
/VREFA: B3.2, C2.1, C3.2, J3.3, J3.4
/VREFB: C7.2, C8.2, C9.1, J4.3, J4.4
GND: J1.2, M1.1, M2.1, M3.1, M4.1
GNDA: A6.2, C2.2, C4.1, C9.2, Con1.2, Con2.1, Con3.2, Con4.1, D2.2, D3.2, D7.2, D8.1, D10.1, Di1.2 (A), Di2.1 (K), J1.1, J2.1, J2.2, J2.9, J2.10, J3.9, J3.10, J4.9, J4.10, J5.1, J5.2
unnamed: A1.2, A2.1, A3.2, A4.1, A5.2, U1.1
unnamed: A2.2, A5.1, B2.1, B3.1, D3.1, U1.2 (-)
unnamed: A3.1, A4.2, C3.1, D1.1, D2.1, U1.3 (+)
unnamed: A7.1, A8.2, C7.1, D8.2, D9.1, U1.5 (+)
unnamed: A9.2, B8.1, B9.1, C8.1, D10.2, U1.6 (-)
unnamed: A7.2, A8.1, A9.1, A10.2, B8.2, U1.7
unnamed: B1.2, B2.2
unnamed: B9.2, B10.2
unnamed: C1.2, D1.2
unnamed: C10.2, D9.2
VCC: A6.1, Con3.1, D4.1, J5.15, J5.16, R1.1, U1.8 (V+)
VSS: C4.2, Con4.2, R2.1, U1.4 (V-)

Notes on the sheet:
MOUNTING HOLES
TO ADC
OUT TO OZDUAL03B_2
RESET

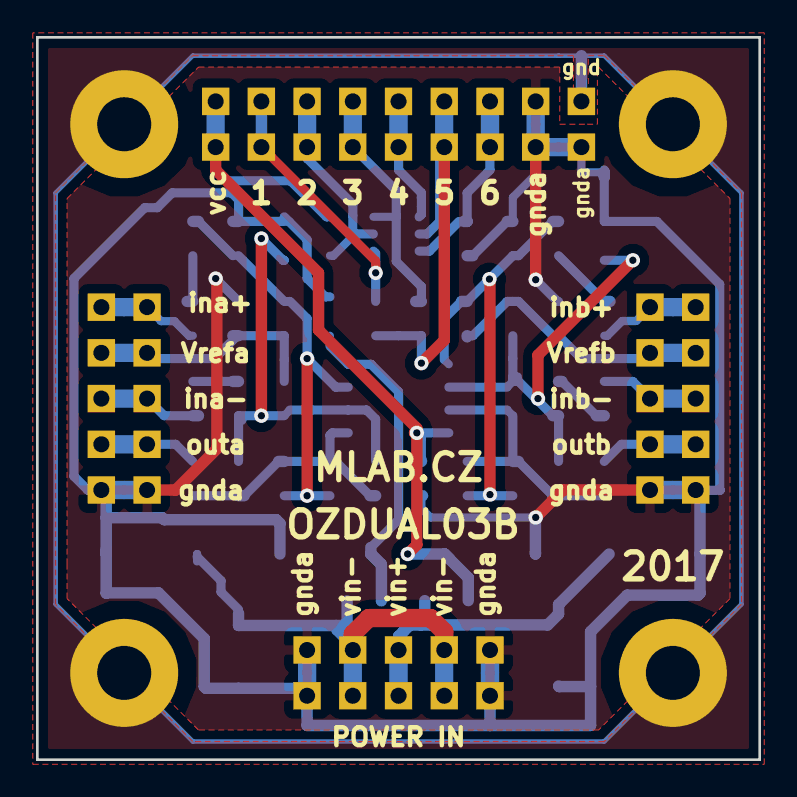
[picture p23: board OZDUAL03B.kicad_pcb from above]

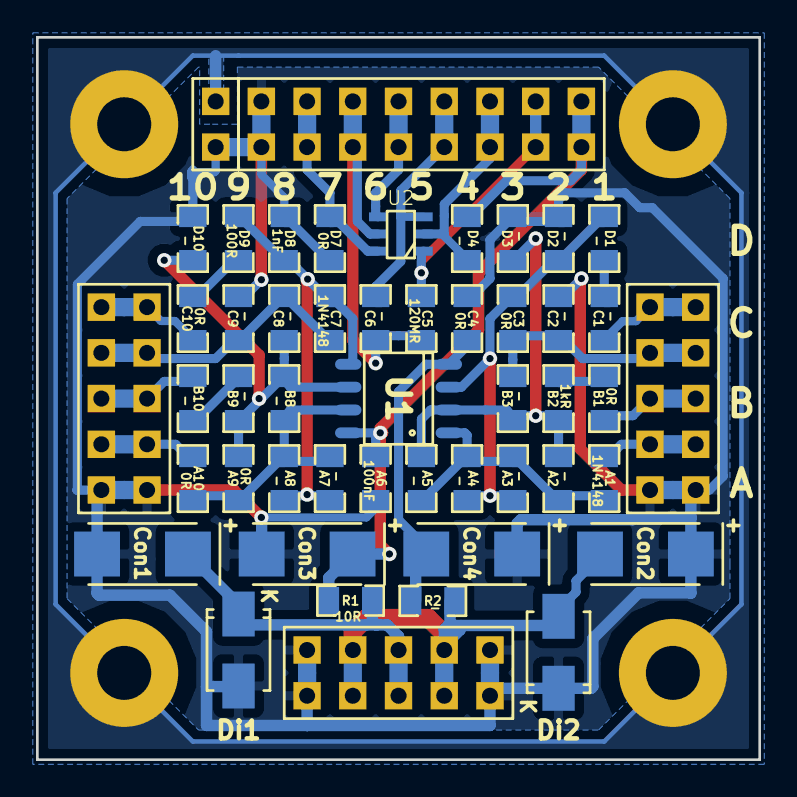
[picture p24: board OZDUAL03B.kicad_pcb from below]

Board: 2 copper layers, 40.1 x 40.1 mm, 53 parts (53 on the bottom side), 30 nets.

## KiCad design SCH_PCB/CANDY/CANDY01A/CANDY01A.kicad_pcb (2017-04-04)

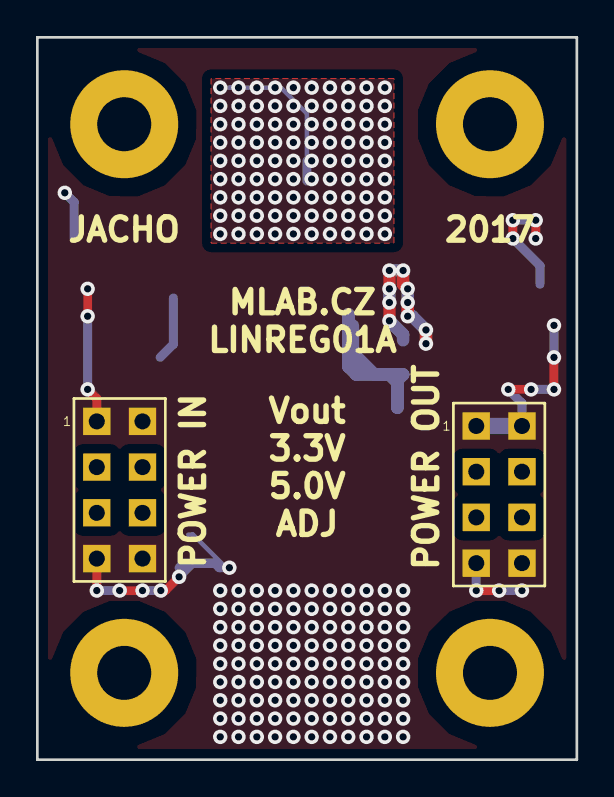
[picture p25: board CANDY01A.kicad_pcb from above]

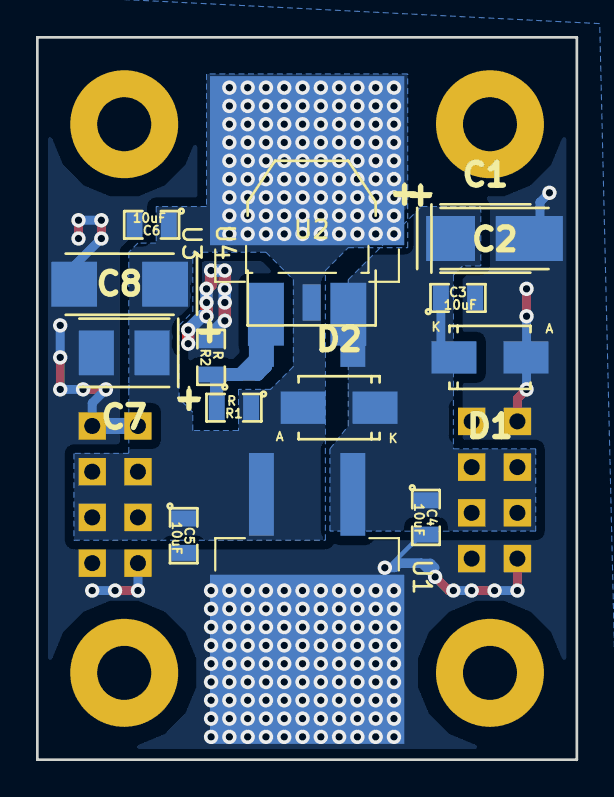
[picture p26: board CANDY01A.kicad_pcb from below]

Board: 2 copper layers, 30.0 x 40.1 mm, 22 parts (16 on the bottom side), 4 nets.

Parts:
C1, C7: CP; TantalC_SizeB_Reflow
C2, C8: CP; TantalC_SizeC_Reflow
C3, C4, C5, C6: 10uF; SMD-0805
D1, D2: M4; Diode-SMA_Standard
J1, J2: HEADER_2x04_PARALLEL; Straight_2x04
M1, M2, M3, M4: HOLE; MountingHole_3mm
R1, R2: R; SMD-0805
U1: L78_DPAK_D2PAK; D2PAK-TO-263-2Lead
U2: LM1117_ADJ_SOT; SOT-223
U3: LM317M_LM217_DPAK_D2PAK; D2PAK-TO-263-2Lead
U4: LM317M_LM217_DPAK_D2PAK; DPAK-TO-252-2Lead

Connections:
/ADJ: R1.2, R2.1, U2.1, U3.1, U4.1
/OUT: C5.1, C6.1, C7.1, C8.1, D2.2, J2.3, J2.4, J2.5, J2.6, R1.1, U1.3, U2.2, U2.4, U3.4, U4.4
GND: C1.2, C2.2, C3.2, C4.2, C5.2, C6.2, C7.2, C8.2, D1.2, J1.1, J1.2, J1.7, J1.8, J2.1, J2.2, J2.7, J2.8, R2.2, U1.4
VCC: C1.1, C2.1, C3.1, C4.1, D1.1, D2.1, J1.3, J1.4, J1.5, J1.6, U1.1, U2.3, U3.3, U4.3

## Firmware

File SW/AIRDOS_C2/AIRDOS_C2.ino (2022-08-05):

//#define DEBUG // Please comment it if you are not debugging
String githash = "$Id$";
/*
  AIRDOS C for tandem with AIRDOS G
 
3 month endurance with LS 33600 = 7.6 mA

ISP
---
PD0     RX
PD1     TX
RESET#  through 50M capacitor to RST#

SDcard
------
DAT3   SS   4 B4
CMD    MOSI 5 B5
DAT0   MISO 6 B6
CLK    SCK  7 B7

ANALOG
------
+      A0  PA0
-      A1  PA1
RESET  0   PB0

LED
---
LED_red  23  PC7         // LED for Dasa


                     Mighty 1284p    
                      +---\/---+
           (D 0) PB0 1|        |40 PA0 (AI 0 / D24)
           (D 1) PB1 2|        |39 PA1 (AI 1 / D25)
      INT2 (D 2) PB2 3|        |38 PA2 (AI 2 / D26)
       PWM (D 3) PB3 4|        |37 PA3 (AI 3 / D27)
    PWM/SS (D 4) PB4 5|        |36 PA4 (AI 4 / D28)
      MOSI (D 5) PB5 6|        |35 PA5 (AI 5 / D29)
  PWM/MISO (D 6) PB6 7|        |34 PA6 (AI 6 / D30)
   PWM/SCK (D 7) PB7 8|        |33 PA7 (AI 7 / D31)
                 RST 9|        |32 AREF
                VCC 10|        |31 GND
                GND 11|        |30 AVCC
              XTAL2 12|        |29 PC7 (D 23)
              XTAL1 13|        |28 PC6 (D 22)
      RX0 (D 8) PD0 14|        |27 PC5 (D 21) TDI
      TX0 (D 9) PD1 15|        |26 PC4 (D 20) TDO
RX1/INT0 (D 10) PD2 16|        |25 PC3 (D 19) TMS
TX1/INT1 (D 11) PD3 17|        |24 PC2 (D 18) TCK
     PWM (D 12) PD4 18|        |23 PC1 (D 17) SDA
     PWM (D 13) PD5 19|        |22 PC0 (D 16) SCL
     PWM (D 14) PD6 20|        |21 PD7 (D 15) PWM
                      +--------+
*/

// Compiled with: Arduino 1.8.5
// MightyCore 2.0.1 https://mcudude.github.io/MightyCore/package_MCUdude_MightyCore_index.json
#include <SD.h>             // Tested with version 1.0.7. (MightyCore)
#include "wiring_private.h"
#include <Wire.h>           // Tested with version 1.0.0.
#include "RTClib.h"         // Tested with version 1.5.4. (NeiroN)

#define LED_red  23 // PC7
#define RESET     0    // PB0
#define HighVoltage  26   // PA2
#define GPSpower  18   // PC2
#define SYNC      19   // PC3
#define SDpower1  1    // PB1
#define SDpower2  2    // PB2
#define SDpower3  3    // PB3
#define SS        4    // PB4
#define MOSI      5    // PB5
#define MISO      6    // PB6
#define SCK       7    // PB7
#define INT       20   // PC4

#define CHANNELS 512   // number of channels in buffer for histogram, including negative numbers
#define GPSerror 70000 // number of cycles for waitig for GPS in case of GPS error 
#define TRESHOLD 3*GPSdelay  // ionising radiation flux treshold for obtaining GPS position

uint16_t count = 0;
uint32_t serialhash = 0;
uint16_t offset, base_offset;
uint8_t lo, hi;
uint16_t u_sensor, maximum;

RTC_Millis rtc;

// Read Analog Differential without gain (read datashet of ATMega1280 and ATMega2560 for refference)
// Use analogReadDiff(NUM)
//   NUM  | POS PIN             | NEG PIN           |   GAIN
//  0 | A0      | A1      | 1x
//  1 | A1      | A1      | 1x
//  2 | A2      | A1      | 1x
//  3 | A3      | A1      | 1x
//  4 | A4      | A1      | 1x
//  5 | A5      | A1      | 1x
//  6 | A6      | A1      | 1x
//  7 | A7      | A1      | 1x
//  8 | A8      | A9      | 1x
//  9 | A9      | A9      | 1x
//  10  | A10     | A9      | 1x
//  11  | A11     | A9      | 1x
//  12  | A12     | A9      | 1x
//  13  | A13     | A9      | 1x
//  14  | A14     | A9      | 1x
//  15  | A15     | A9      | 1x
#define PIN 0
uint8_t analog_reference = INTERNAL2V56; // DEFAULT, INTERNAL, INTERNAL1V1, INTERNAL2V56, or EXTERNAL

void setup()
{

  // Open serial communications and wait for port to open:
  Serial.begin(9600);
  while (!Serial) 
  {
  ; // wait for serial port to connect. Needed for Leonardo only?
  }

  Serial.println("#Cvak...");
  
  ADMUX = (analog_reference << 6) | ((PIN | 0x10) & 0x1F);
  
  ADCSRB = 0;               // Switching ADC to Free Running mode
  sbi(ADCSRA, ADATE);       // ADC autotrigger enable (mandatory for free running mode)
  sbi(ADCSRA, ADSC);        // ADC start the first conversions
  sbi(ADCSRA, 2);           // 0x100 = clock divided by 16, 62.5 kHz, 208 us for 13 cycles of one AD conversion, 24 us fo 1.5 cycle for sample-hold
  cbi(ADCSRA, 1);        
  cbi(ADCSRA, 0);        

  pinMode(RESET, OUTPUT);   // reset for peak detetor

  //pinMode(SDpower1, OUTPUT);  // SDcard interface
  //pinMode(SDpower2, OUTPUT);     
  //pinMode(SDpower3, OUTPUT);     
  //pinMode(SS, OUTPUT);     
  //pinMode(MOSI, INPUT);     
  //pinMode(MISO, INPUT);     
  //pinMode(SCK, OUTPUT);  

  DDRB = 0b10011110;
  PORTB = 0b00000000;  // SDcard Power OFF

  DDRA = 0b11111100;
  PORTA = 0b00000000;  // SDcard Power OFF
  DDRC = 0b11100000;
  PORTC = 0b00000000;  // SDcard Power OFF
  DDRD = 0b11111100;
  PORTD = 0b00000000;  // SDcard Power OFF

  pinMode(LED_red, OUTPUT);
  digitalWrite(LED_red, LOW);  
  digitalWrite(RESET, LOW);  
  
  //!!! Wire.setClock(100000);

  for(int i=0; i<5; i++)  
  {
    delay(50);
    digitalWrite(LED_red, HIGH);  // Blink for Dasa 
    delay(50);
    digitalWrite(LED_red, LOW);  
  }

  Serial.println("#Hmmm...");

  // make a string for device identification output
  String dataString = "$AIRDOS,C," + githash.substring(5,45) + ","; // FW version and Git hash

/*!!!  
  Wire.beginTransmission(0x58);                   // request SN from EEPROM
  Wire.write((int)0x08); // MSB
  Wire.write((int)0x00); // LSB
  Wire.endTransmission();
  Wire.requestFrom((uint8_t)0x58, (uint8_t)16); 
*/   
  for (int8_t reg=0; reg<16; reg++)
  { 
    uint8_t serialbyte = 0xFF; //!!!  Wire.read(); // receive a byte
    if (serialbyte<0x10) dataString += "0";
    dataString += String(serialbyte,HEX);    
    serialhash += serialbyte;
  }

  {
    DDRB = 0b10111110;
    PORTB = 0b00001111;  // SDcard Power ON
  
    // make sure that the default chip select pin is set to output
    // see if the card is present and can be initialized:
    if (!SD.begin(SS)) 
    {
      Serial.println("#Card failed, or not present");
      // don't do anything more:
      return;
    }
  
    // open the file. note that only one file can be open at a time,
    // so you have to close this one before opening another.
    File dataFile = SD.open("datalog.txt", FILE_WRITE);
  
    // if the file is available, write to it:
    if (dataFile) 
    {
      dataFile.println(dataString);  // write to SDcard (800 ms)     
      dataFile.close();
  
      digitalWrite(LED_red, HIGH);  // Blink for Dasa
      Serial.println(dataString);  // print SN to terminal 
      digitalWrite(LED_red, LOW);          
    }  
    // if the file isn't open, pop up an error:
    else 
    {
      Serial.println("#error opening datalog.txt");
    }
  
    DDRB = 0b10011110;
    PORTB = 0b00000001;  // SDcard Power OFF          
  } 

  // measurement of ADC offset
  ADMUX = (analog_reference << 6) | 0b10001; // Select +A1,-A1 for offset correction
  delay(200);
  ADCSRB = 0;               // Switching ADC to Free Running mode
  sbi(ADCSRA, ADATE);       // ADC autotrigger enable (mandatory for free running mode)
  sbi(ADCSRA, ADSC);        // ADC start the first conversions
  sbi(ADCSRA, 2);           // 0x100 = clock divided by 16, 62.5 kHz, 208 us for 13 cycles of one AD conversion, 24 us fo 1.5 cycle for sample-hold
  cbi(ADCSRA, 1);
  cbi(ADCSRA, 0);
  sbi(ADCSRA, ADIF);                  // reset interrupt flag from ADC
  while (bit_is_clear(ADCSRA, ADIF)); // wait for the first conversion
  sbi(ADCSRA, ADIF);                  // reset interrupt flag from ADC
  lo = ADCL;
  hi = ADCH;
  ADMUX = (analog_reference << 6) | 0b10000; // Select +A0,-A1 for measurement
  ADCSRB = 0;               // Switching ADC to Free Running mode
  sbi(ADCSRA, ADATE);       // ADC autotrigger enable (mandatory for free running mode)
  sbi(ADCSRA, ADSC);        // ADC start the first conversions
  sbi(ADCSRA, 2);           // 0x100 = clock divided by 16, 62.5 kHz, 208 us for 13 cycles of one AD conversion, 24 us fo 1.5 cycle for sample-hold
  cbi(ADCSRA, 1);
  cbi(ADCSRA, 0);
  // combine the two bytes
  u_sensor = (hi << 7) | (lo >> 1);
  // manage negative values
  if (u_sensor <= (CHANNELS / 2) - 1 ) {
    u_sensor += (CHANNELS / 2);
  } else {
    u_sensor -= (CHANNELS / 2);
  }
  base_offset = u_sensor;

}
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

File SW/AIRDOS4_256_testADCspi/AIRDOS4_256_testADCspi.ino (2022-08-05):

// 3 mesice s LS 33600 = 7.6 mA
/*
  CANDY based on Mighty 1284p with RTC
 
Compiled with: Arduino 1.8.3

ISP
---
PD0     RX
PD1     TX
RESET#  through 50M capacitor to RST#

SDcard
------
DAT3   SS   4 B4
CMD    MOSI 5 B5
DAT0   MISO 6 B6
CLK    SCK  7 B7

SERIAL 2 (not necessary to connect)
--------
RX 18 PC2
TX 19 PC3

ANALOG
------
+      A0  PA0
-      A1  PA1
RESET  0   PB0

RELE
----
RELE_ON   11    PD3
RELE_OFF  12    PD4

LED
---
LED_yellow  23  PC7         // LED pro Dasu
LED_green   TIMEPULSE GPS   // LED pro pilota

The following needs to be added to the line mentioning the atmega644 in
/usr/share/arduino/libraries/SD/utility/Sd2PinMap.h:

    || defined(__AVR_ATmega1284P__)

so that it reads:

    #elif defined(__AVR_ATmega644P__) || defined(__AVR_ATmega644__)|| defined(__AVR_ATmega1284P__) 
    
                      +---\/---+
           (D 0) PB0 1|        |40 PA0 (AI 0 / D24)
           (D 1) PB1 2|        |39 PA1 (AI 1 / D25)
      INT2 (D 2) PB2 3|        |38 PA2 (AI 2 / D26)
       PWM (D 3) PB3 4|        |37 PA3 (AI 3 / D27)
    PWM/SS (D 4) PB4 5|        |36 PA4 (AI 4 / D28)
      MOSI (D 5) PB5 6|        |35 PA5 (AI 5 / D29)
  PWM/MISO (D 6) PB6 7|        |34 PA6 (AI 6 / D30)
   PWM/SCK (D 7) PB7 8|        |33 PA7 (AI 7 / D31)
                 RST 9|        |32 AREF
                VCC 10|        |31 GND
                GND 11|        |30 AVCC
              XTAL2 12|        |29 PC7 (D 23)
              XTAL1 13|        |28 PC6 (D 22)
      RX0 (D 8) PD0 14|        |27 PC5 (D 21) TDI
      TX0 (D 9) PD1 15|        |26 PC4 (D 20) TDO
RX1/INT0 (D 10) PD2 16|        |25 PC3 (D 19) TMS
TX1/INT1 (D 11) PD3 17|        |24 PC2 (D 18) TCK
     PWM (D 12) PD4 18|        |23 PC1 (D 17) SDA
     PWM (D 13) PD5 19|        |22 PC0 (D 16) SCL
     PWM (D 14) PD6 20|        |21 PD7 (D 15) PWM
                      +--------+
*/

#include "wiring_private.h"
//#include <SoftwareSerial.h>


#define MSG_NO 20    // number of logged NMEA messages

#define RELE_ON     11    // PD3
#define RELE_OFF    12    // PD4
#define LED_yellow  23    // PC7

#define CONV  1
#define SCK   2
#define SDI   3

#define CHANNELS 512 // number of channels in buffer for histogram, including negative numbers

//SoftwareSerial swSerial(18, 19); // RX, TX

const int chipSelect = 4;
int RESET = 0;
uint16_t count = 0;


void setup()
{

  // Open serial communications and wait for port to open:
  Serial.begin(9600);
  while (!Serial) 
  {
  ; // wait for serial port to connect. Needed for Leonardo only?
  }

  //swSerial.begin(115200);
  Serial.println("#Cvak...");
  
// Read Analog Differential without gain (read datashet of ATMega1280 and ATMega2560 for refference)
// Use analogReadDiff(NUM)
//   NUM	|	POS PIN	  	        |	NEG PIN		        | 	GAIN
//	0	|	A0			|	A1			|	1x
//	1	|	A1			|	A1			|	1x
//	2	|	A2			|	A1			|	1x
//	3	|	A3			|	A1			|	1x
//	4	|	A4			|	A1			|	1x
//	5	|	A5			|	A1			|	1x
//	6	|	A6			|	A1			|	1x
//	7	|	A7			|	A1			|	1x
//	8	|	A8			|	A9			|	1x
//	9	|	A9			|	A9			|	1x
//	10	|	A10			|	A9			|	1x
//	11	|	A11			|	A9			|	1x
//	12	|	A12			|	A9			|	1x
//	13	|	A13			|	A9			|	1x
//	14	|	A14			|	A9			|	1x
//	15	|	A15			|	A9			|	1x
  #define pin 0
  uint8_t analog_reference = INTERNAL2V56; // DEFAULT, INTERNAL, INTERNAL1V1, INTERNAL2V56, or EXTERNAL

  ADMUX = (analog_reference << 6) | ((pin | 0x10) & 0x1F);

  pinMode(RESET, OUTPUT);     
  pinMode(RELE_ON, OUTPUT);
  pinMode(RELE_OFF, OUTPUT);
  pinMode(LED_yellow, OUTPUT);
  digitalWrite(LED_yellow, HIGH);  
  
  digitalWrite(RELE_ON, LOW);  // Rele switch OFF
  digitalWrite(RELE_OFF, HIGH);  
  delay(500);
  digitalWrite(RELE_OFF, LOW);

  pinMode(CONV, OUTPUT);
  pinMode(SCK, OUTPUT);
  pinMode(SDI, INPUT);
  digitalWrite(CONV, LOW);
  digitalWrite(SCK, HIGH);

  for(int i=0; i<20; i++)  
  {
    delay(50);
    digitalWrite(LED_yellow, LOW);  // Blink for Dasa 
    delay(50);
    digitalWrite(LED_yellow, HIGH);  
  }
  
  Serial.println("#Hmmm...");
}

#define MEASUREMENTS  25  // cca 5 minutes of radiation measurement

void loop()
{
  for(int x=0; x<MEASUREMENTS; x++)  
  {
    uint8_t lo, hi;
    uint16_t u_sensor;
    //int16_t s_sensor;
    uint16_t buffer[CHANNELS];
    
    for(int n=0; n<CHANNELS; n++)
    {
      buffer[n]=0;
    }
    
    digitalWrite(RESET, HIGH);   // Reset peak detector
    digitalWrite(RESET, HIGH);   // Reset peak detector
    digitalWrite(RESET, HIGH);   // Reset peak detector
    digitalWrite(RESET, HIGH);   // Reset peak detector
    digitalWrite(RESET, HIGH);   // Reset peak detector
    digitalWrite(RESET, HIGH);   // Reset peak detector
    digitalWrite(RESET, HIGH);   // Reset peak detector
    digitalWrite(RESET, HIGH);   // Reset peak detector
    digitalWrite(RESET, HIGH);   // Reset peak detector
    digitalWrite(RESET, HIGH);   // Reset peak detector
    for (int i=0; i<20; i++) {digitalWrite(RESET, LOW);} // compensate first data aquisition cca 100 us

    uint16_t maximum = 0;  
    uint16_t supress = 0;      

    //!!! for(uint16_t n=0; n<65535; n++) // cca 12 s
    for(uint16_t n=0; n<65535; n++)
    {
      for (int i=0; i<15; i++) {digitalWrite(RESET, LOW);} // whole integration cca 200 us

      // Hold peak detector
      //pinMode(RESET, OUTPUT);     
      //digitalWrite(RESET, LOW); 
      //digitalWrite(RESET, HIGH); 

      digitalWrite(CONV, HIGH);
      delayMicroseconds(5);
      digitalWrite(CONV, LOW);
      digitalWrite(RESET, HIGH); 
      digitalWrite(RESET, LOW); 

      u_sensor = 0;
      digitalWrite(SCK, LOW);
      digitalWrite(SCK, HIGH);
      if (digitalRead(SDI)) bitSet(u_sensor, 8);
      digitalWrite(SCK, LOW);
      digitalWrite(SCK, HIGH);
      if (digitalRead(SDI)) bitSet(u_sensor, 7);
      digitalWrite(SCK, LOW);
      digitalWrite(SCK, HIGH);
      if (digitalRead(SDI)) bitSet(u_sensor, 6);
      digitalWrite(SCK, LOW);
      digitalWrite(SCK, HIGH);
      if (digitalRead(SDI)) bitSet(u_sensor, 5);
      digitalWrite(SCK, LOW);
      digitalWrite(SCK, HIGH);
      if (digitalRead(SDI)) bitSet(u_sensor, 4);
      digitalWrite(SCK, LOW);
      digitalWrite(SCK, HIGH);
      if (digitalRead(SDI)) bitSet(u_sensor, 3);
      digitalWrite(SCK, LOW);
      digitalWrite(SCK, HIGH);
      if (digitalRead(SDI)) bitSet(u_sensor, 2);
      digitalWrite(SCK, LOW);
      digitalWrite(SCK, HIGH);
      if (digitalRead(SDI)) bitSet(u_sensor, 1);
      digitalWrite(SCK, LOW);
      digitalWrite(SCK, HIGH);
      if (digitalRead(SDI)) bitSet(u_sensor, 0);


      // manage negative values
      //if (u_sensor <= 511 ) {u_sensor += 512;} else {u_sensor -= 512;}
      //if (u_sensor <= (CHANNELS/2)-1 ) {u_sensor += (CHANNELS/2);} else {u_sensor -= (CHANNELS/2);}
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

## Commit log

2017-03-31 Tvorba podkladů
    [OZDUAL03A.kicad_pcb, OZDUAL03A.sch]
2017-04-03 vykres OZDUAL03A
    [OZDUAL03A.dxf]
2017-04-03 New battery holder.
    [MLAB_logo.scad, flexbatter.scad, flexbatter.stl]
2017-04-18 Edit schema
    [CANDY01A.sch]
2017-08-16 Add files via upload
    circuit improvements.
2017-09-04 revise of schematic
    [CANDY01A.sch]
2017-09-07 Adding design of 3D printed shielding box.
    [Box.scad, Box.stl, BoxBase.scad, BoxBase.stl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]
2017-09-11 Box for AIRDOS - without strenghtening crossbars.
    [Box.scad, Box.stl]
2017-09-14 Battery holder
    [AIRDOS_batter.scad, P_AIRDOS_batter_belt.scad, P_AIRDOS_batter_belt.stl, P_AIRDOS_batter_body.scad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]
2017-09-14 flexbatter side grip overhang enabled.
    [P_AIRDOS_batter_body.stl, assembly.scad, flexbatter.scad]
2017-09-15 Edit batter holder
    [AIRDOS_batter.scad, P_AIRDOS_batter_body.stl, flexbatter.scad]
2017-09-15 New stl
    [P_AIRDOS_batter_body.stl]
2017-10-06 Data editing
    update schema, new label
    [CANDY01A.sch, OZDUAL03A.kicad_pcb, OZDUAL03B.kicad_pcb, OZDUAL03B.sch]
2017-10-09 New device labels.
2017-10-09 New suggestion for device label.
2017-10-18 change schematics R11/D5 R12
    [CANDY01A.sch]
2017-10-20 resizing to 18mm printing height.
2017-10-20 resizing to 18mm height
2017-10-21 new document describing device labeling
2017-11-04 adding new photos of AIRDOS device.
2017-11-04 Device photo enhancement.
2017-12-08 Draw scheme
    [OZDUAL03B.csv, OZDUAL03B.kicad_pcb, OZDUAL03B.sch]
2018-06-01 calibrated version
2018-11-18 more power saving for AIRDOS_G, data logging only high fluxes
